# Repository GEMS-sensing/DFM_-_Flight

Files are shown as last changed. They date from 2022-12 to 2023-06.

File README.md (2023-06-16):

# Project-Flight_DFM
Manufacturing information for the Flight system 

#### [Flight_Assembly_BoM](Flight_Assembly_BoM.csv)
Bill of Materials for full system assembly 

#### Custom Parts Required:
- [Logger Box](./Box)
- [Mounting Plate](./Box)

#### Sub Assemblies Required:
- [Kestrel Board, v1.9](https://github.com/gemsiot/DFM_-_Kestrel)
- [Gonk Board, v1.2](https://github.com/gemsiot/DFM_-_Gonk-18650-1S3P)
- [SDI-12 Talon, v1.4](https://github.com/gemsiot/DFM_-_Talon-SDI12)
- [I2C Talon, v2.1](https://github.com/gemsiot/DFM_-_Talon-I2C)
- [Aux Talon, v1.5](https://github.com/gemsiot/DFM_-_Talon-Aux)

## System Assembly

- All parts required for system assembly are detailed in [Flight_Assembly_BoM](Flight_Assembly_BoM.csv)
- After all sub assemblies are finished, complete the following steps 
1. Prepare main data logger board using assembly instructions detailed in [Kestrel Assembly Video](https://drive.google.com/open?id=1bD3Pa5R_5ufvpw4cUTz-tKCreJj2a7cN&authuser=schu3119%40umn.edu&usp=drive_fs)
2. Prepare mounting plate (if necessary) using instructions detailed in [Mounting Plate Prep Video](https://drive.google.com/open?id=1bFxcQoePnDuSZhUtLkiAZ8WnBKMtT0PU&authuser=schu3119%40umn.edu&usp=drive_fs)
3. Place antennas onto the mounting plate as detailed in [Antenna Placement Video](https://drive.google.com/open?id=1bRhHP4KZSppHAmR2KgFZIg572g8hdObi&authuser=schu3119%40umn.edu&usp=drive_fs)
4. Attach first layer of components to mounting plate as detailed in [Mounting Plate Assembly](https://drive.google.com/open?id=1bT006Io6QUtz_VcvTtEhTx-1zirhanhX&authuser=schu3119%40umn.edu&usp=drive_fs)
5. Install Talon boards into logger box as detailed in [Talon Install](https://drive.google.com/open?id=1bXs4N-supN-SKw3k3KqC6i_FpCVYv-39&authuser=schu3119%40umn.edu&usp=drive_fs)
	- __All Talon nuts should be torqued to 1.0Nm__
6. Install cable gland in logger box as detailed in [Cable Gland Install](https://drive.google.com/open?id=1baKlFoLFSimpsM3mUY0MrUyb_E4Ifo47&authuser=schu3119%40umn.edu&usp=drive_fs)
	- __Cable gland should be tightened to logger box with torque of 1.6Nm__
7. Install prepared mounting plate into logger box as detailed in [Mounting Plate Install](https://drive.google.com/open?id=1aQjAO0VGxeccukH69H0SHO_HMsZDXyN0&authuser=schu3119%40umn.edu&usp=drive_fs)
8. Install prepared main data logger as detailed in [Kestrel Install](https://drive.google.com/open?id=1aqM2ey-8seV0-pxXx1Z-ZSsXYQLJVgyQ&authuser=schu3119%40umn.edu&usp=drive_fs)
	- __Switch nut should be tightened with a torque of 0.7Nm__
	- __USB screws should be tightened with a torque of 0.3Nm__
9. Make connections between main data logger and Talons using cable assemblies as described in [Talon Cable Connection](https://drive.google.com/open?id=1b7LckyKWHlNqdWrOU5_O6cfOPqYJ8c6I&authuser=schu3119%40umn.edu&usp=drive_fs)
10. Perform final assembly steps given detailed description in [Final Assembly](https://drive.google.com/open?id=1bCYssfYtOqvqFnKVWkBEIiFjV94_6-FX&authuser=schu3119%40umn.edu&usp=drive_fs)
	- __Cable gland cap should be tightened with a torque of 1.0Nm__
	- __Lid screws should be tightened with a torque of 0.9Nm__

## System Registration/Testing

1. Connect logger to computer using micro USB cable
2. Switch logger on using external switch
3. Run provided registration program 
	- Assign name with sequential numbering which matches label on boards 
4. Receive conformation of success from registration program
5. Unplug logger from computer and set aside
6. Wait for self-test to complete, ensure LEDs do not indicate any failure
	- If no failure indication: shut down logger, assembly process is completed
	- If failure is indicated: review logger output and confirm system assembly

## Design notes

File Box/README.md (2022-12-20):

#### [WC-24F_v3_Body_Printing](WC-24F_v3_Body_Printing.pdf) 
Printing file for the WC-24F housing made by Polycase (printing to be done by Polycase)

#### [WC-24F_v3_Body_v005](WC-24F_v3_Body_v005.zip)
Zipped version of STEP file.
Milling file for the the WC-24F housing made by Polycase (milling to be done by Polycase)

#### [WC-24F_v3_MountingPLate_v003_LASER](WC-24F_v3_MountingPLate_v003_LASER.dxf)
Laser cut file for mounting plate, blue lines are vector cut, red lines are vector engrave. Intended for production by Ponoko 

#### [Print WC-24F_v3_MountingPlate_v003_LASER](Print%20WC-24F_v3_MountingPlate_v003_LASER.pdf)
**PROOF FILE - NOT FOR MANUFACTURE** This file is a 1:1 scale PDF of the mounting plate outline, used to confirm correct rendering for production 

#### [WC-24F_v3_MountingPlate_v004_DRAWING](WC-24F_v3_MountingPlate_v004_DRAWING.pdf)
**PROOF FILE - NOT FOR MANUFACTURE** This file is a dimentional drawing of the mouting plate, used to confirm correct rendering for production. The perimeter of this model is identical to v003 mounting plate, but thickness has been adjusted to match production model.

#### [WC-24F_v3_Body_v005_DRAWING](WC-24F_v3_Body_v005_DRAWING.pdf)
**PROOF FILE - NOT FOR MANUFACTURE** This file is a dimentional drawing of the milled out box, used to confirm correct rendering for production.

## Mounting Plate
__Manufacturer:__ Ponoko

__Material:__ Clear Acrylic, 0.12" Thick

__File:__ [WC-24F_v3_MountingPLate_v003_LASER.dxf](WC-24F_v3_MountingPLate_v003_LASER.dxf)

See ordering example below

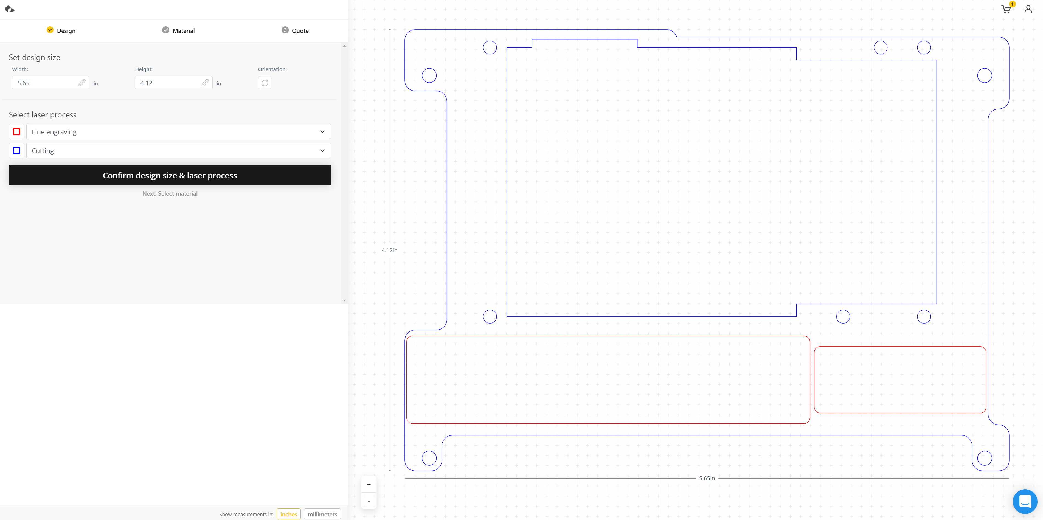
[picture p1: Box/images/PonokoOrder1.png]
Order Page 1

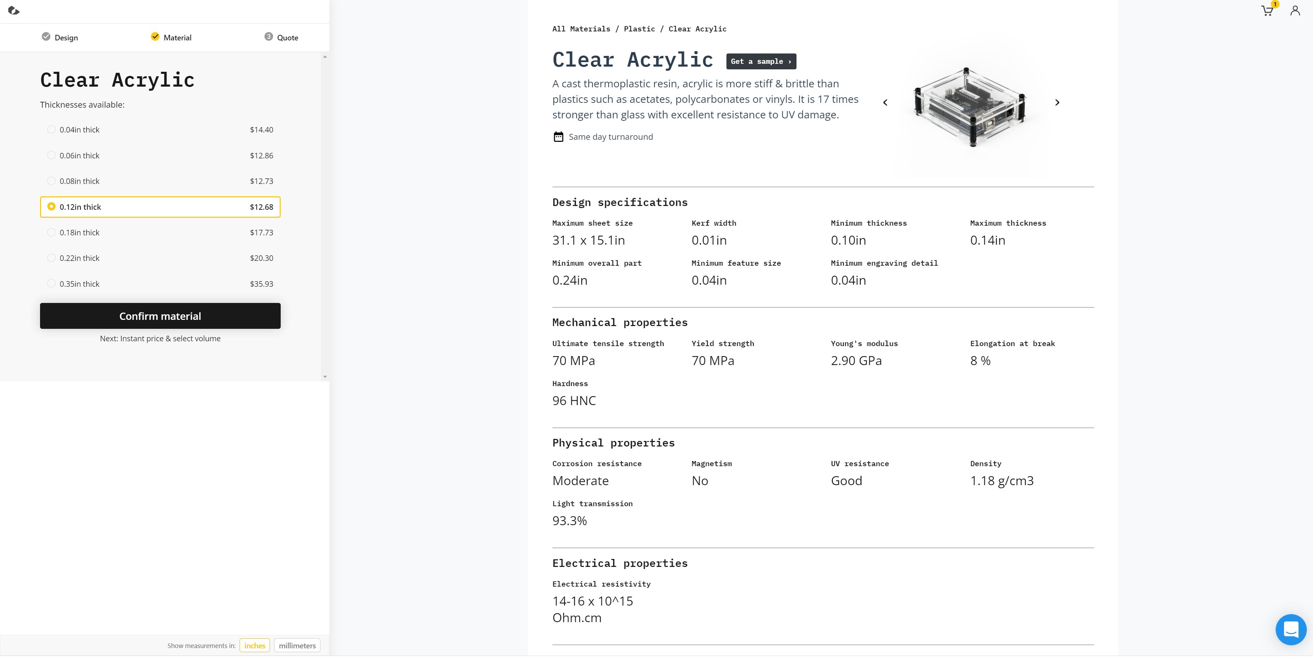
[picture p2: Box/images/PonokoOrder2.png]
Order Page 2

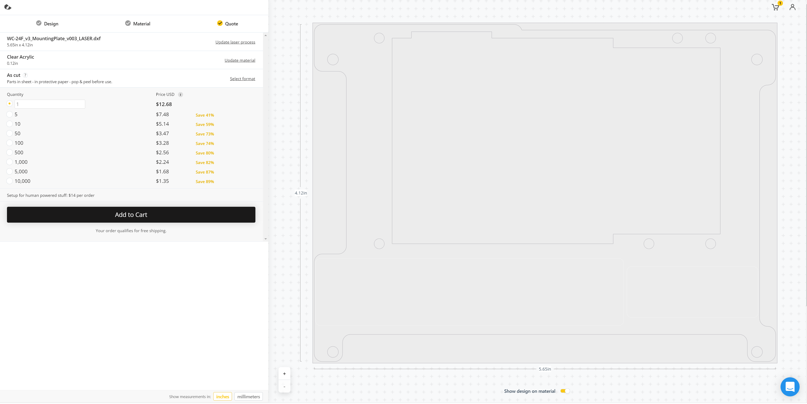
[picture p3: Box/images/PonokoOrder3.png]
Order Page 3


Red lines are intended to be an outline, no engraving inside this area is intended. 

## Box
__Manufacturer:__ Polycase

__Base Part:__ WC-24F

__File, Milling:__ [WC-24F_v3_Body_v005.STEP](WC-24F_v3_Body_v005.zip)

__File, Printing:__ [WC-24F_v3_Body_Printing.pdf](WC-24F_v3_Body_Printing.pdf) [^1]

[^1]: Note: The printing PDF lists the part as `W_-24BF`, this simply indicates that the outline file is the same for the WC-24F and the WP-24F. The 'B' indicates that this is the outline for the _bottom_ of the two part design. __The part number for ordering is WC-24F.__

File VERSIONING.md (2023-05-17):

## System Versioning 

### v3.0B
- v3.0A version with fix to Kestrel TCXO overvoltage 
- TCXO overvoltage fixed with retrofit described in [Kestrel issue #19](https://github.com/gemsiot/Project-Kestrel/issues/19)

### v3.0A
- First production version with fix to Kestrel SAFE MODE circuit
- SAFE MODE circuit patched to be electrically equivalent to Kestrel v1.7

### v3.0
- First production units
- Fall 2022

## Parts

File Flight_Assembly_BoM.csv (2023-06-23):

Item | Make | Model | Part Number | Qty | Notes
Kestrel Logger Board | Caltronics | MainLogger_1v9 | N/A | 1
I2C Talon | Caltronics | Talon_I2C_2v1 | N/A | 1
SDI-12 Talon | Caltronics | Talon_SDI12_1v4 | N/A | 1
Aux Talon | Caltronics | AuxTalon_LoadSwitch_1v5 | N/A | 1
Battery Holder - Gonk | Caltronics | 18650_1S3P_Smart_VertCon_1v2 | N/A | 1
Mounting Plate | Custom | WC-24F_v3_MountingPlate_v003 | N/A | 1
Box | Polycase | WC-24F_v3_Body_v005 | N/A | 1
SoM Controller | Particle | B404X | B404XMEA | 1
Screw, SoM | Generic | Button Head Hex Drive Screw Passivated 18-8 Stainless Steel, M2 x 0.40 mm Thread, 3mm Long | 92095A276 | 1 | McMaster Part Number
Washer, SoM | Generic | 18-8ÿStainless Steel Washer for M2ÿScrewÿSize,ÿ2.2ÿmmÿID,ÿ5 mm OD | 93475A195 | 1 | McMaster Part Number
Battery | Panasonic | NCR18650B | NCR18650B | 3 | Flat top
Solar Connector | Voltaic Systems | Female 3.5x1.1mm - JST Extension | W058 | 1
Cable Gland | Amphenol | CABLE GLAND 3-6.5MM M12 NYLON | AIO-CSM12 | 1
USB Cover | Amphenol | Rugged Dust Cover for MicroUSB | MUSB2K15015BP | 1
Screw, USB | Generic | Stainless Steel Button Head Hex Drive Screw 2-56 Thread Size, 5/16" Long | 92949A078 | 2 | McMaster Part Number
Micro SD Card | SanDisk | Ultra microSD | SDSQUNC-016G-AN6MA | 1
Cable, Short | Molex | MICROLOCK PLUS CABLE BLACK 6 CKT | 451110600 | 2
Cable, Long | Molex | MICROLOCK PLUS CABLE BLACK 6 CKT | 451110601 | 1
Cable, Battery | Molex | MICROFIT 6 CIRCUIT 150MM | 451320601 | 1
Screw, Nylon | Generic | Nylon socket head, 4-40, 1/4" | 95868A256 | 10 | McMaster Part Number
Nut | Generic | Nylon hex nut, 4-40 | 94812A200 | 2 | McMaster Part Number
Standoff | Generic | Female threaded hex standoff, aluminium, 3/16" hex, 1" long, 4-40 | 91780A537 | 4 | McMaster Part Number
Screw, Thread Forming | Generic | Rounded Head Thread-Forming Screws for Brittle Plastic, 18-8 Stainless Steel, Number 4 Size, 1/4" Long | 97349A415 | 4 | McMaster Part Number
Desicant | Generic | Silica gel desiccant bags for 235 cubic inches | 2189K46 | 1 | McMaster Part Number

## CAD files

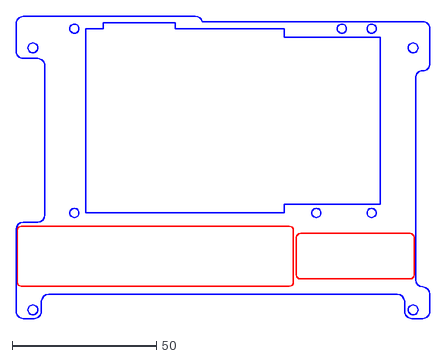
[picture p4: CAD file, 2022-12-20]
Box/WC-24F_v3_MountingPlate_v003_LASER.dxf
143.6 x 104.8

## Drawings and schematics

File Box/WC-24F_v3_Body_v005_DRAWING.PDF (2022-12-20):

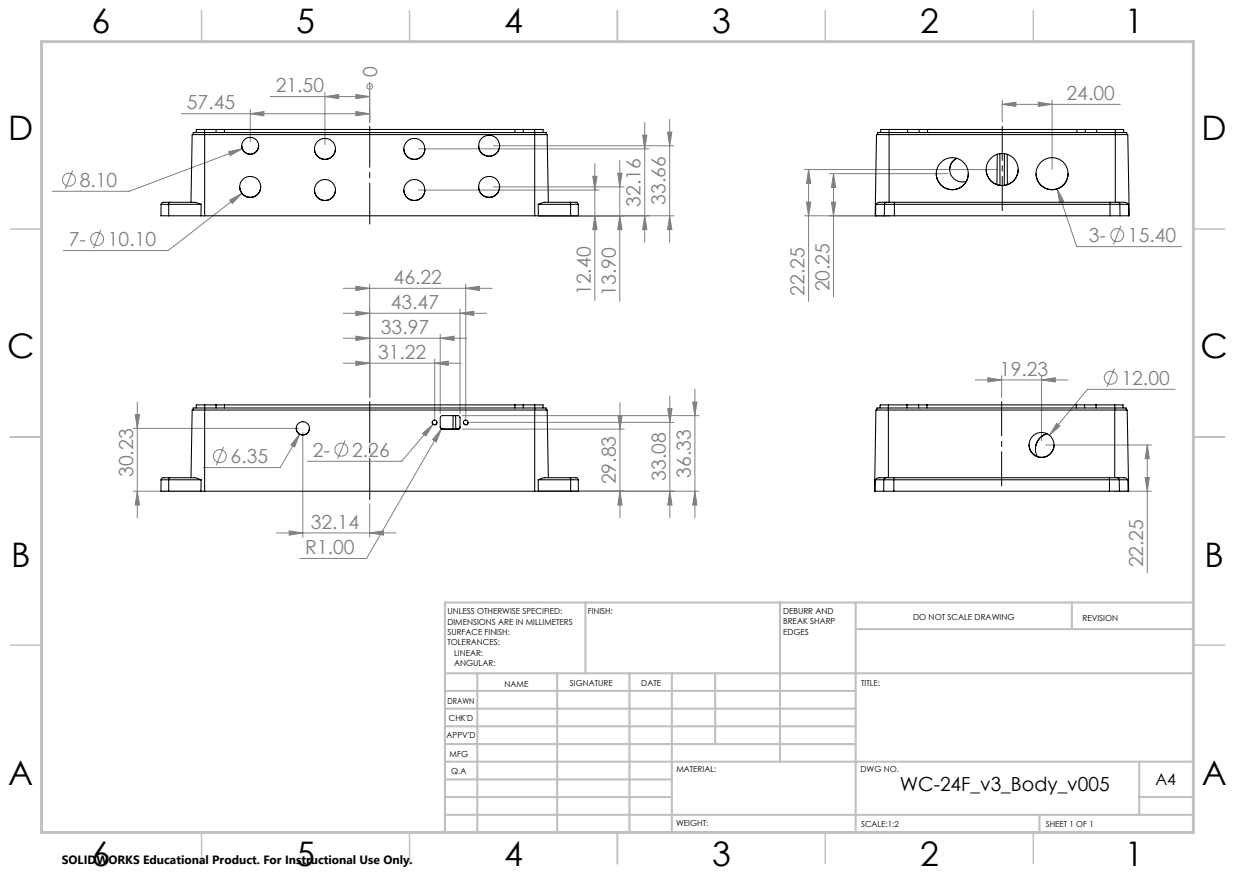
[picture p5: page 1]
FINISH:; DEBURR AND; BREAK SHARP; DO NOT SCALE DRAWING; REVISION; SCALE:1:2; SHEET 1 OF 1

UNLESS OTHERWISE SPECIFIED:
DIMENSIONS ARE IN MILLIMETERS
SURFACE FINISH:
TOLERANCES:
LINEAR:
ANGULAR:

NAME | SIGNATURE | DATE | | | | TITLE:

DRAWN
CHK'D
APPV'D
MFG
Q.A | | | | MATERIAL: | DWG NO. WC-24F_v3_Body_v005 | A4

SOLIDWORKS Educational Product. For Instructional Use Only.

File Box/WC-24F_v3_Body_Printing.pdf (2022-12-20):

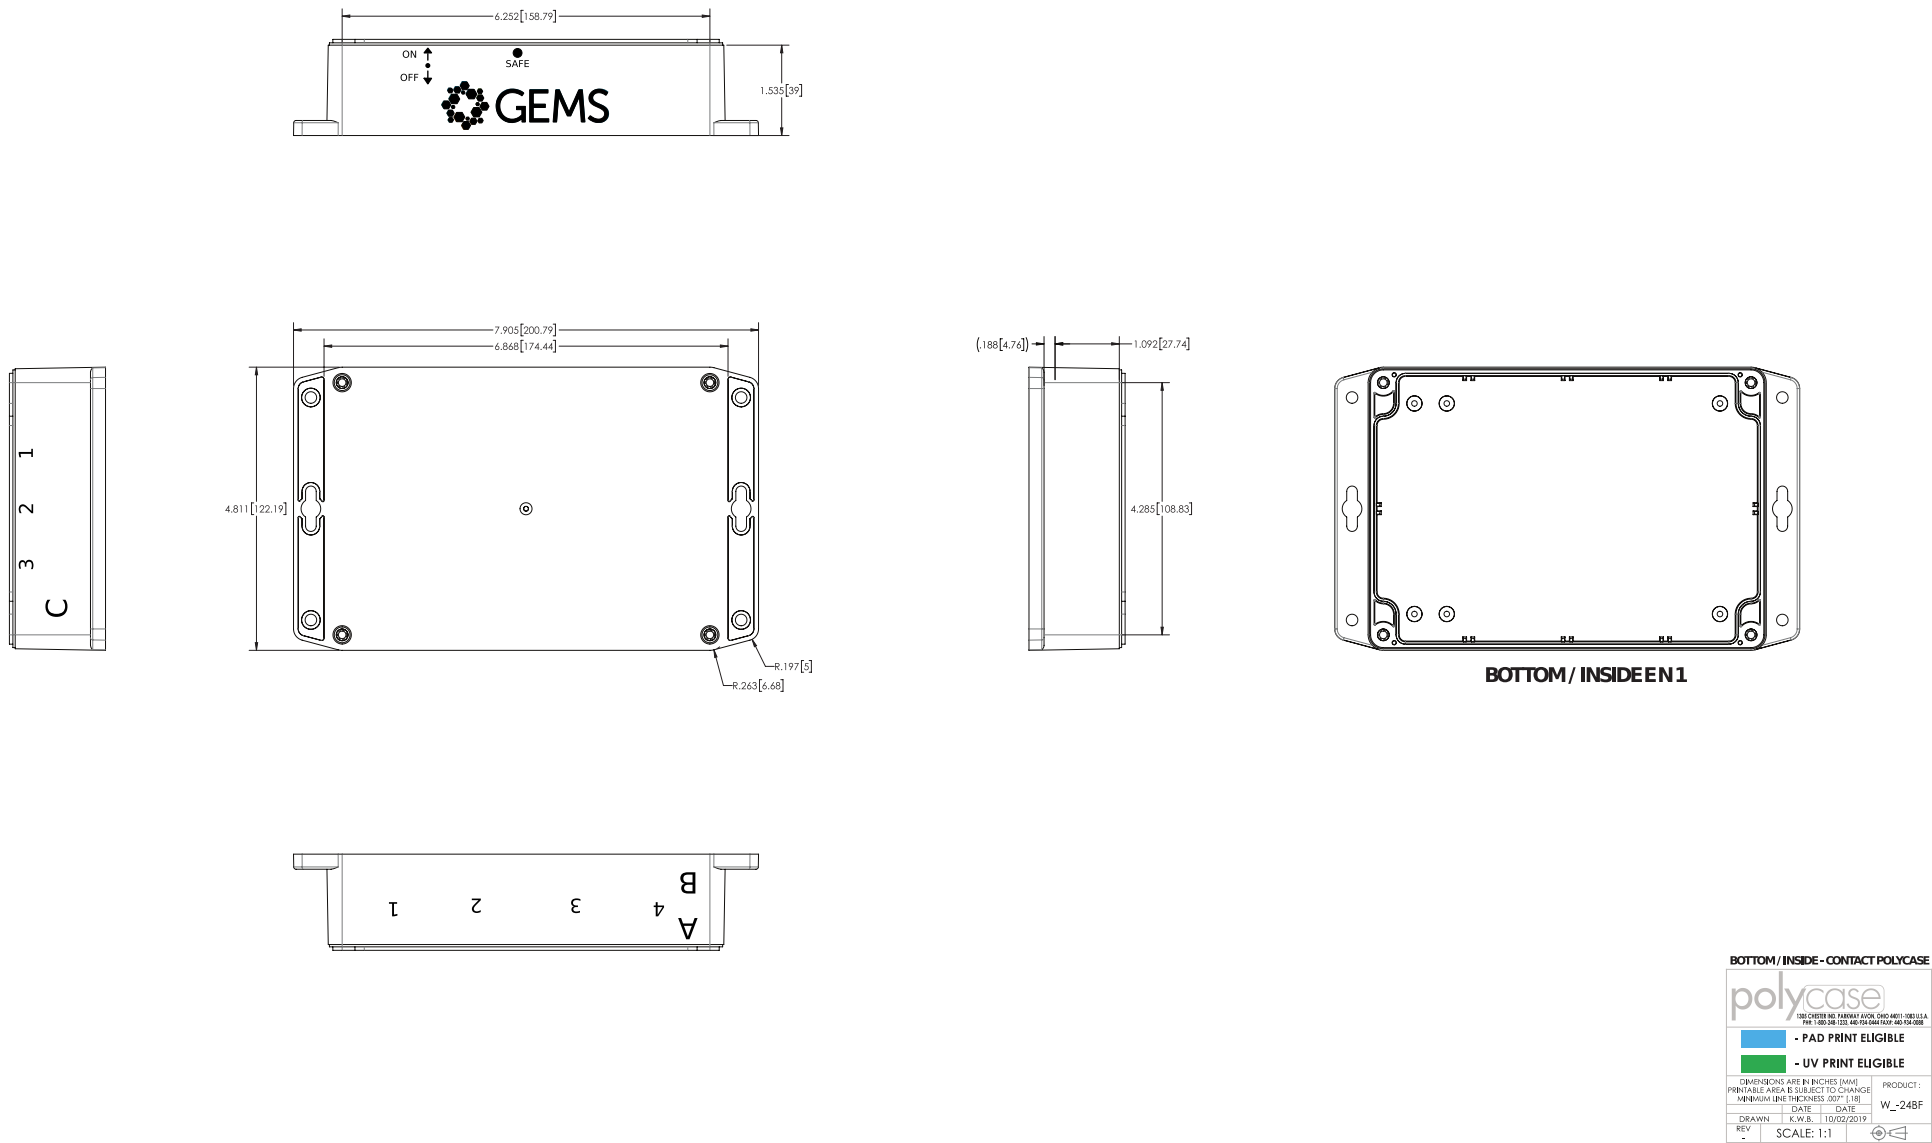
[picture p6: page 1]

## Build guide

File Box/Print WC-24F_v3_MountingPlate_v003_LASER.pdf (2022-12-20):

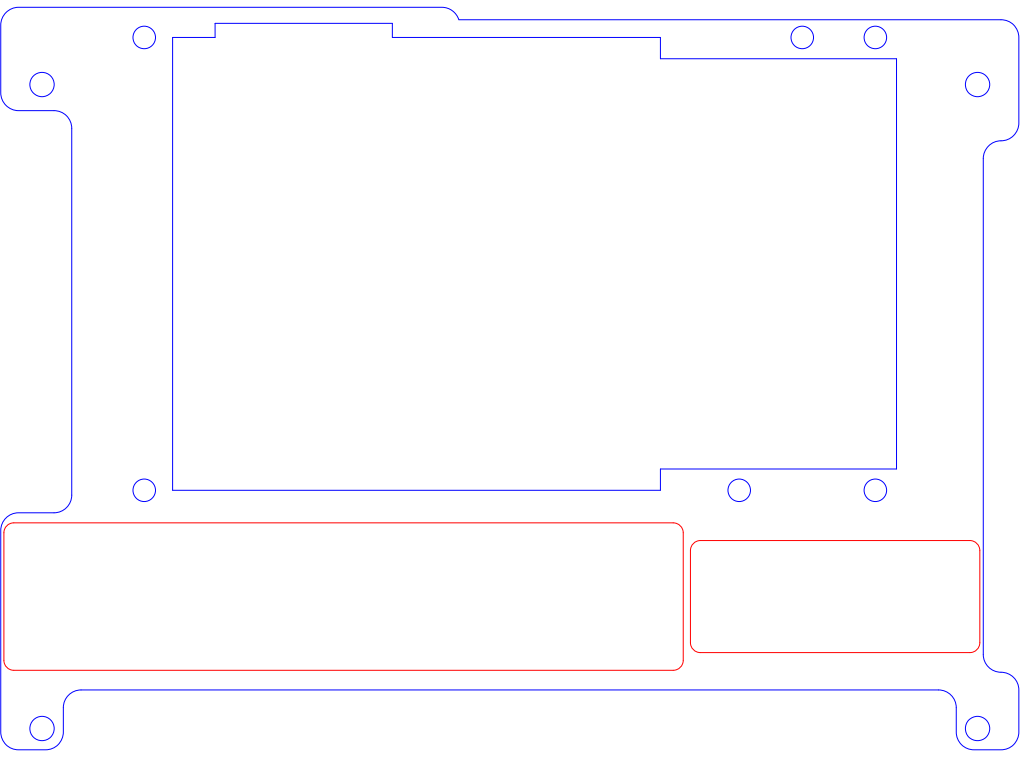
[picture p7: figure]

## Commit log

2022-12-20 Initial additions
    [WC-24F_v3_MountingPlate_v003_LASER.dxf]
2023-01-06 Added general BoM, added main readme
    [Flight_Assembly_BoM.csv]
2023-01-09 Added note about device registration
2023-05-10 Updated for v1.8 Kestrel and v1.5 Aux Talon
    Updated README and BoM to reflect v1.8 Kestrel update and v1.5 Aux Talon update
    [Flight_Assembly_BoM.csv]
2023-06-23 Fixed Kestrel version in BoM
    Fixed Kestrel version listed in BoM, should have been v1.9, was listed as v1.8 still
    [Flight_Assembly_BoM.csv]
